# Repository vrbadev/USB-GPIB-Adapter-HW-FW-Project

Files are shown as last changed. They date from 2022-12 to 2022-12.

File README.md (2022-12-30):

# USB-GPIB Adapter (HW & FW)
 A complete hardware and firmware design of a custom USB-GPIB adapter. This project was created as a part of a semestral work of a [Virtual Instrumentation course (B3M38VIN)](https://intranet.fel.cvut.cz/en/education/bk/predmety/46/82/p4682806.html) at the Czech Technical University.

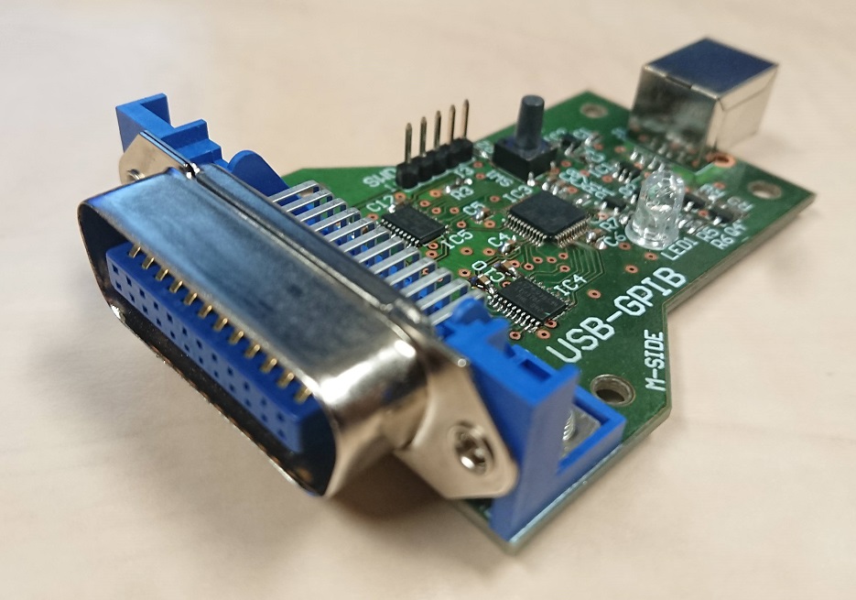
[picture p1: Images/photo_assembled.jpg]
The assembled USB-GPIB Adapter board. The assembled USB-GPIB Adapter board


## Repository Contents

* **Hardware folder** - Contains complete Altium Designer 6 PCB project, including PDF schematic and layout visualisations.
* **Firmware folder** - Contains complete Keil uVision project with the firmware for the STM32F103C6T6 microcontroller.
* **Gerber ZIP file** - An archive containing generated production files for the PCB.

## Motivation

The General Purpose Interface Bus (GPIB) is one of the most widely used communication interfaces for laboratory measuring and testing instruments. It was developed in 1965 by Hewlett-Packard (which is why it is sometimes referred to as HP-IB) and was later adopted as the IEEE 488 standard in 1975, gradually evolving into the current IEEE 488.2 standard in 1992. It also defined the SCPI (Standard Commands for Programmable Instruments) command structures, which now form a single and universal set of commands for controlling all instruments connected to this bus.

To connect the bus to the user's computer, however, a GPIB interface module is required, which is available for virtually all important types of computer buses, such as PCI or USB plug-in cards. However, both cables and GPIB interface modules (adapters) are very expensive, as they are used with expensive professional devices from companies such as Rhode & Schwartz, B&K Precision, Tektronix, HP, etc. They have no application in the mainstream consumer industry. To give a more realistic idea, Figs. 1 and 2 show commercial USB-GPIB adapters whose prices are in the tens of thousands of CZK. 

In the images below: [National Instruments GPIB-USB-HS adapter](https://cz.farnell.com/ni/778927-01/gpib-instrument-control-device/dp/3621284) (left) and [Keysight 82357B Interface USB-to-GPIB](https://cz.farnell.com/keysight-technologies/82357b/converter-interface-usb-to-gpib/dp/1425679) (right).

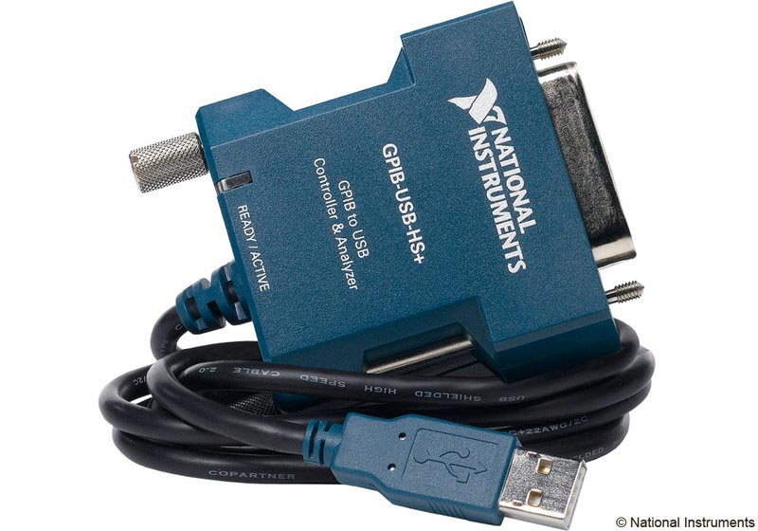
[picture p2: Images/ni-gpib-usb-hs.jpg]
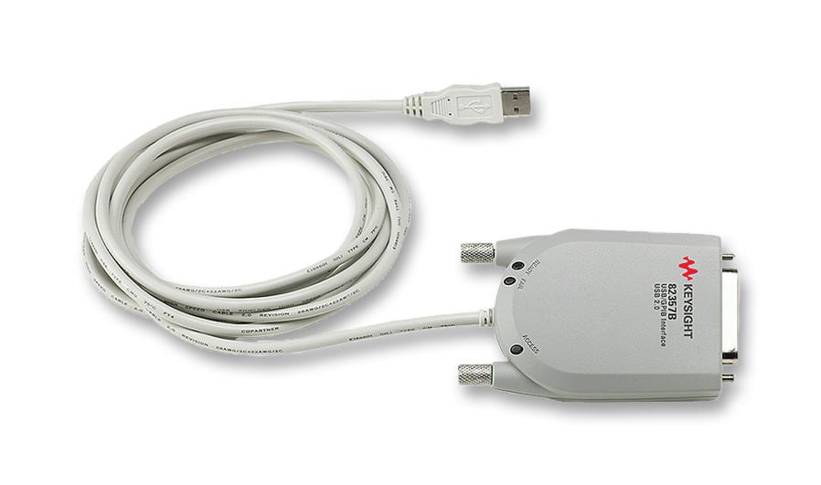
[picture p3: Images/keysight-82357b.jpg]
 

<p style="clear:both;">

For this reason, many open-source alternatives to commercial USB-GPIB adapters have already been developed that can be easily assembled and used without major problems with all laboratory instruments  with GPIB interfaces. This paper deals with the design of a similar adapter from commercially available components and is inspired by [this GitHub project](https://github.com/xyphro/UsbGpib).
</p>

## Basic Description of GPIB

GPIB is a parallel bus, i.e. each subsequent measuring instrument can be connected via a double-sided GPIB connector to the connector plugged into the previous instrument. In this way, up to 14 instruments can be connected together without a control counter (adapter). It supports a transfer rate of max. 1 MB/s. [[Tutorial Description of the Hewlett-Packard Interface Bus](http://www.bitsavers.org/pdf/hp/hpib/TutorialDescrOfHPIB.pdf)]

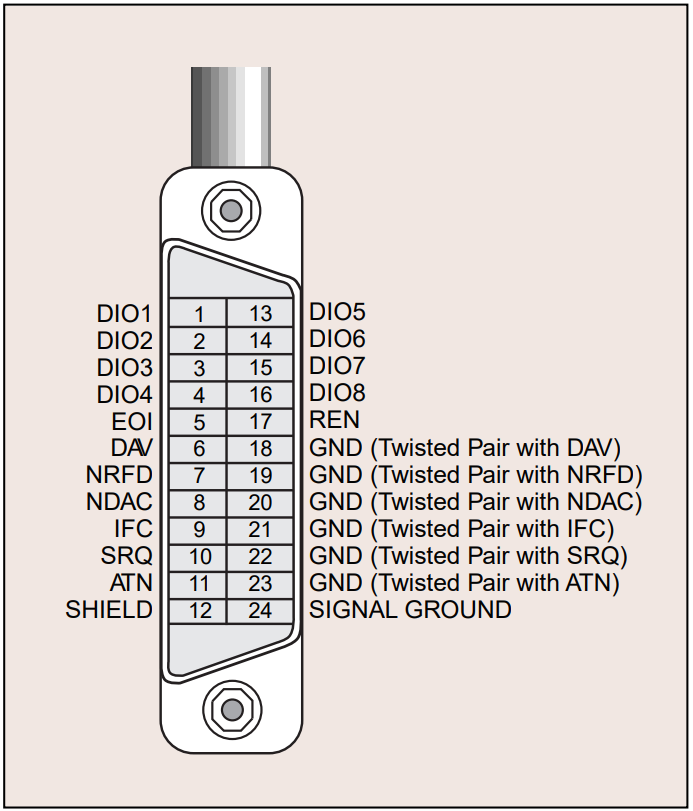
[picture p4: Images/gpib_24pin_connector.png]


The standard GPIB connector is also labeled Centronics and uses 24 wires, as indicated in the image on right (taken from the [GPIB Tutorial](http://lmu.web.psi.ch/docu/manuals/software_manuals/GPIB/GPIB_tutorial.pdf)). Eight of the 24 wires are used for grounding and the remaining wires can be divided into 3 groups:
* **8 data wires** labeled DIO1 to DIO8. They are used for data and command transmission (depending on the state of the ATN wire). All commands and most data use the 7-bit ASCII/ISO set, therefore DIO8 can be used for parity.
* **3 handshaking wires** are used for asynchronous control of the byte transfer of individual messages between devices and guarantee error-free transmission. They are NRFD (not ready for data) controlled by the receiver, NDAC (not data accepted) also controlled by the receivers and DAV (data valid) controlled by the data senders.
* **5 control wires** for controlling the flow of information through the bus, namely:
    - ATN (attention) - the Controller sets to log 1 if a command is sent over the data wires.
    - IFC (interface clear) - uses the Controller to control activity on the bus.
    - REN (remote enable) - controlled by the Controller to provide remote control.
    - SRQ (service request) - can be used by any device for asynchronous controller service request.
    - EOI (end or indentify) - used by the Talker to indicate the end of a sent message, also used by the Controller.

The bus uses inverse TTL logic, i.e. if the state of the lines is log 1 (High), the corresponding voltage is less or equal 0.8	V. The inverse of the state log. 0 (Low) corresponds to a voltage greater or equal 2.0 V. To ensure high transmission speeds, conductor lengths and distances between devices are limited, a maximum cable length of 15 m is specified, all devices should use three-state logic (log 0, log 1 and Hi-Z high impedance state) and the capacitance of each conductor should be less or equal 50 pF.

The devices connected to the GPIB bus can be divided into 3 groups:
* **Talker**, which sends data to listeners (if prompted by the Controller).
* **Listener**, which receives data (if prompted by the Controller).
* **Controller**, which manages the data flow over the bus by means of commands sent to other connected devices. Only one active Controller can be connected to the bus at a time (Controller-in-Charge, CIC).

One device (e.g. a multimeter) can be both a Talker and a Listener. The USB-GPIB adapter is the bus Controller.

### Handshaking Protocol
In the original version of the 488.1 standard, it was necessary for each Listener to set the NRFD to log. 0, then the Talker set DAV to log 1 to indicate to the Listener that data was available, and finally the Listener set NDAC to log. 0 after receiving a byte of data, as in the left figure below (taken from the [GPIB Tutorial](http://lmu.web.psi.ch/docu/manuals/software_manuals/GPIB/GPIB_tutorial.pdf)). This caused a time delay of T1 before the whole process could be repeated and another byte of data could be sent.

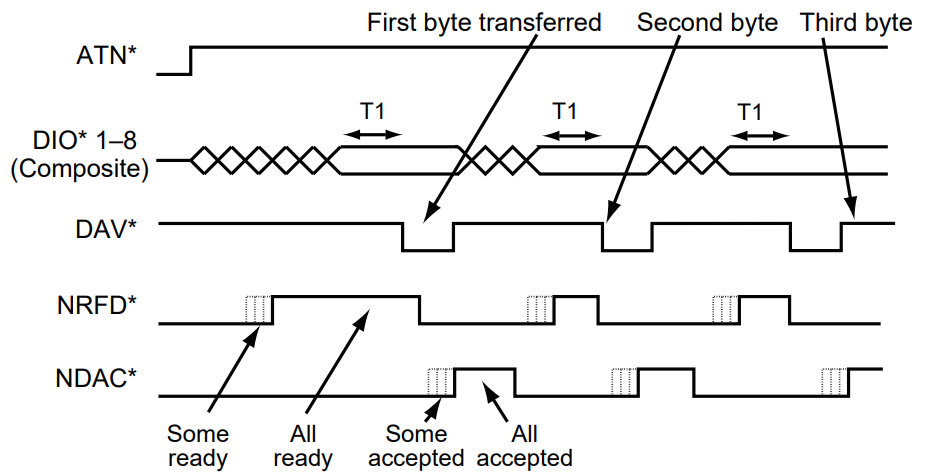
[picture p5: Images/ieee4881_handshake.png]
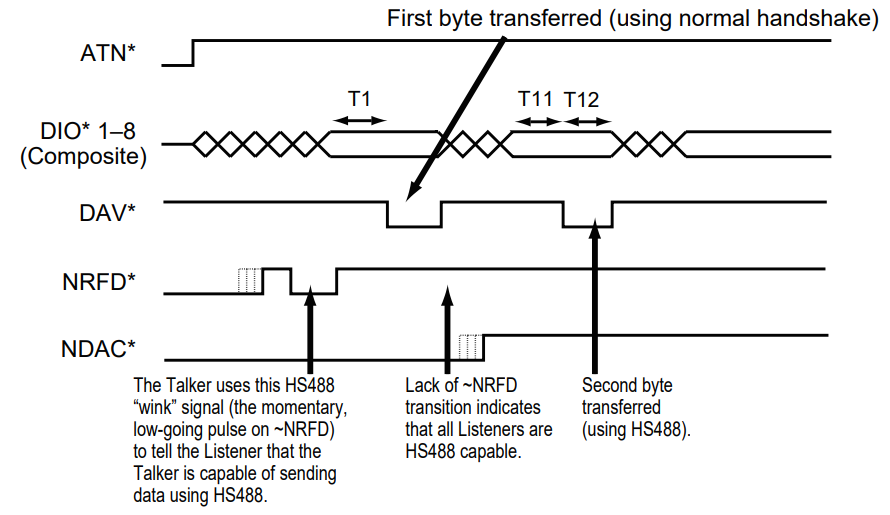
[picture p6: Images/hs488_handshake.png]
 

<p style="clear:both;">

To accelerate data transfer (up to 8 MB/s) over the GPIB bus, National Instruments developed the High-Speed GPIB Handshake Protocol called HS488. In this case, the Talker first creates a pulse (log 0) on the NRFD wire (after the controller addresses all listeners) to indicate that it can use HS488. Then the Talker moves the first byte to the data wires, waits the preset time, and sets DAV to log 1. Then it waits again, sets DAV to log. 0 and moves the next byte to the data wires, as in the right figure above (taken from the [GPIB Tutorial](http://lmu.web.psi.ch/docu/manuals/software_manuals/GPIB/GPIB_tutorial.pdf)). The Listener leaves the NDAC in log. 1 and must be able to receive single bytes at the preset delays. The Listener can pause the byte transmission by setting the NDAC to log. 0. If the Listener does not support HS488 and wants to use the normal handshake protocol, it creates a pulse log. 0 on the NRFD line.
</p>

Due to the hardware nature of this project, I will not describe further here the control commands and sequences of the cont- roler, protocols (composed of multiple control sequences), the SCPI language, or other software aspects of the GPIB bus.

## Adapter Hardware Design

[The aforementioned GitHub project](https://github.com/xyphro/UsbGpib) uses the [ATMega32U4 microcontroller from Microchip](https://www.microchip.com/content/dam/mchp/documents/OTH/ProductDocuments/DataSheets/Atmel-7766-8-bit-AVR-ATmega16U4-32U4_Datasheet.pdf). This 8-bit microprocessor offers 32 kB of FLASH memory and 2.5 kB of SRAM memory and is based on the AVR architecture. It contains a USB peripheral, an internal 8 MHz oscillator and a maximum core operating frequency of 16 MHz (16 MIPS). The advantage is the power supply voltage of a 5 V and the corresponding voltage tolerance of the GPIO pins in the input and output configuration.

For my design I chose the [STM32F103C6T6 microprocessor from STMicroelectronics](https://www.st.com/resource/en/datasheet/stm32f103c6.pdf). It is a 32-bit microprocessor also with 32 kB of FLASH memory and 10 kB of SRAM memory, built on ARM architecture with Cortex-M3 core. It also offers a USB peripheral and an internal 8 MHz RC oscillator that can be used with an integrated PLL to obtain a maximum operating frequency of 72 MHz. However, it must be powered from 3.3 V and most GPIOs are 5 V tolerant (denoted FT) in the input configuration only. I selected it for the easy soldering of its LQFP48 package.

### USB Connector

For connecting USB peripherals, I chose a USB 2.0 B female connector, which is standard for USB endpoint devices. To provide ESD protection, a [USBLC6-2 component from STMicroelectronics](http://www.st.com/resource/en/datasheet/usblc6-2.pdf) is added. The wiring diagram is shown below.

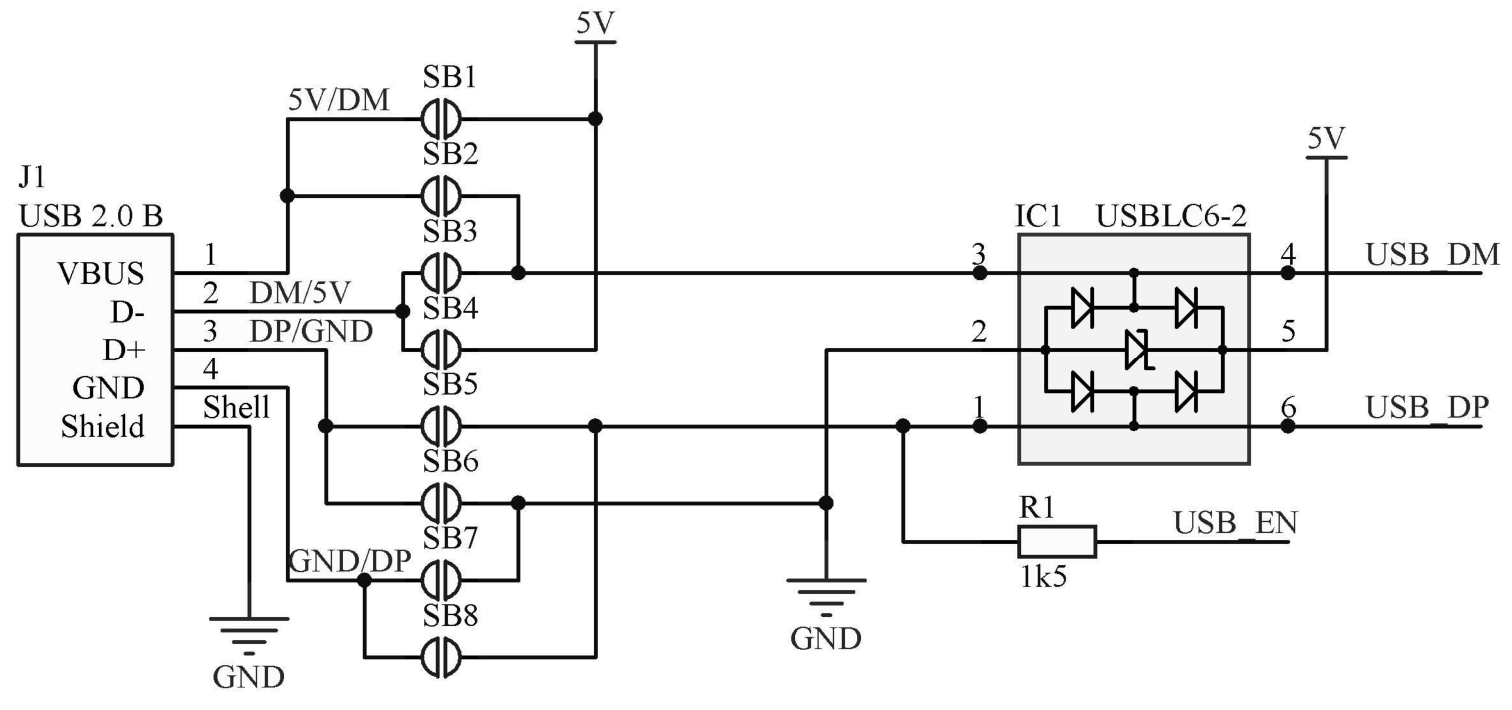
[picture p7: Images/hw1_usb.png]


The USB_DM and USB_DP lines are connected directly to the microprocessor. The USB_EN line with a 1.5kOhm pull-up resistor on the USB D+ line is used to trigger enumeration as a Full-Speed USB Device (according to the USB FS specification), since STM32 microprocessors do not internally contain this resistor.

To be able to use GPIB socket or plug and thus to fit components from both sides (the socket pins are axially inverted to the plug pins), I made the PCB design axially symmetrical in respect to the placement of THT components. Because if the USB connector is soldered from the other side, the +5V contact is then swapped with GND, similarly D- with D+, so shorting jumpers SB1 to SB8 are added to resolve this problem. These jumpers (i.e. odd or even) should be closed on the side of the PCB where the USB connector will be mounted.

### Power Circuit

To obtain 3.3 V from 5 V (USB) I chose a linear regulator with output current up to 300 mA, low dropout, minimum quiescent current and fixed output voltage, [LDK130 from STMicroelectronics](https://www.st.com/resource/en/datasheet/ldk130.pdf). Blocking capacitors of 100 nF are added at all power supply pins of the ICs in the circuit. The schematic is shown in figure below.

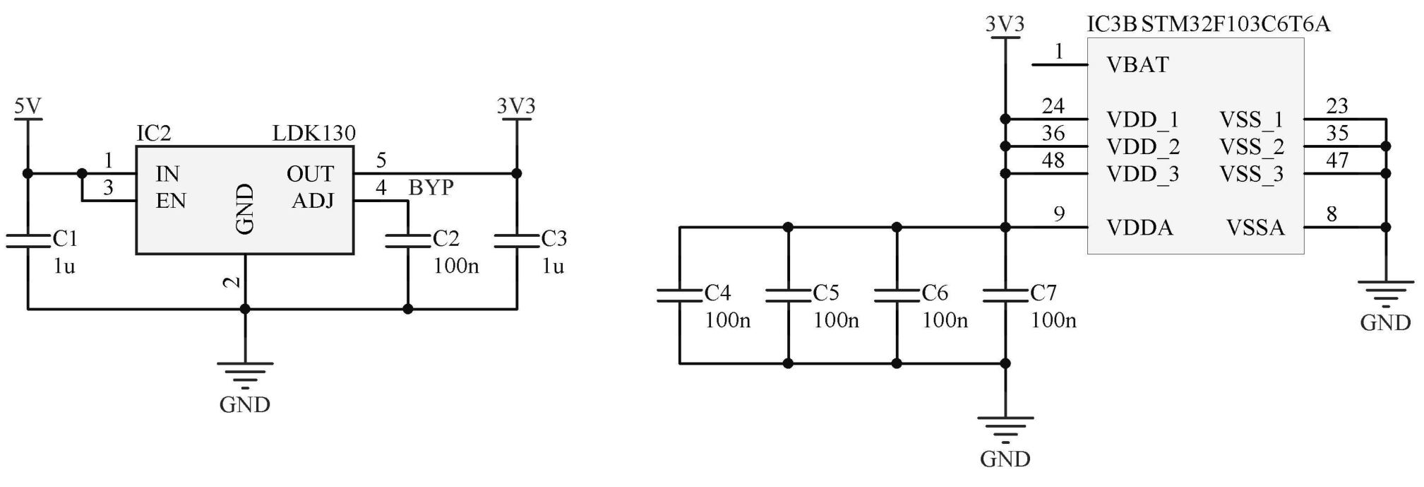
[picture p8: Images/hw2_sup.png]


### STM32 Microcontroller

Since the internal RC oscillator is be used, pins PD0 and PD1 remain unconnected. Pull-up resistor R2 keeps log. 1 on the reset pin of the microcontroller and button SW1 is used to ground and reset it, capacitor C8 is placed here to filter out mechanical oscillations of the button. Pull-down resistor R3 on the BOOT0 pin is used to initially load the program from the microprocessor's FLASH memory.

STM32 processors are programmed via the SWD interface and the ST-Link programmer, which consists of the SWDCLK and SWDIO pins in addition to the reset pin, power and ground. These 5 wires are routed through the J3 connector in the same order as they are found, for example, on Nucleo boards. The wiring of this part is shown below.

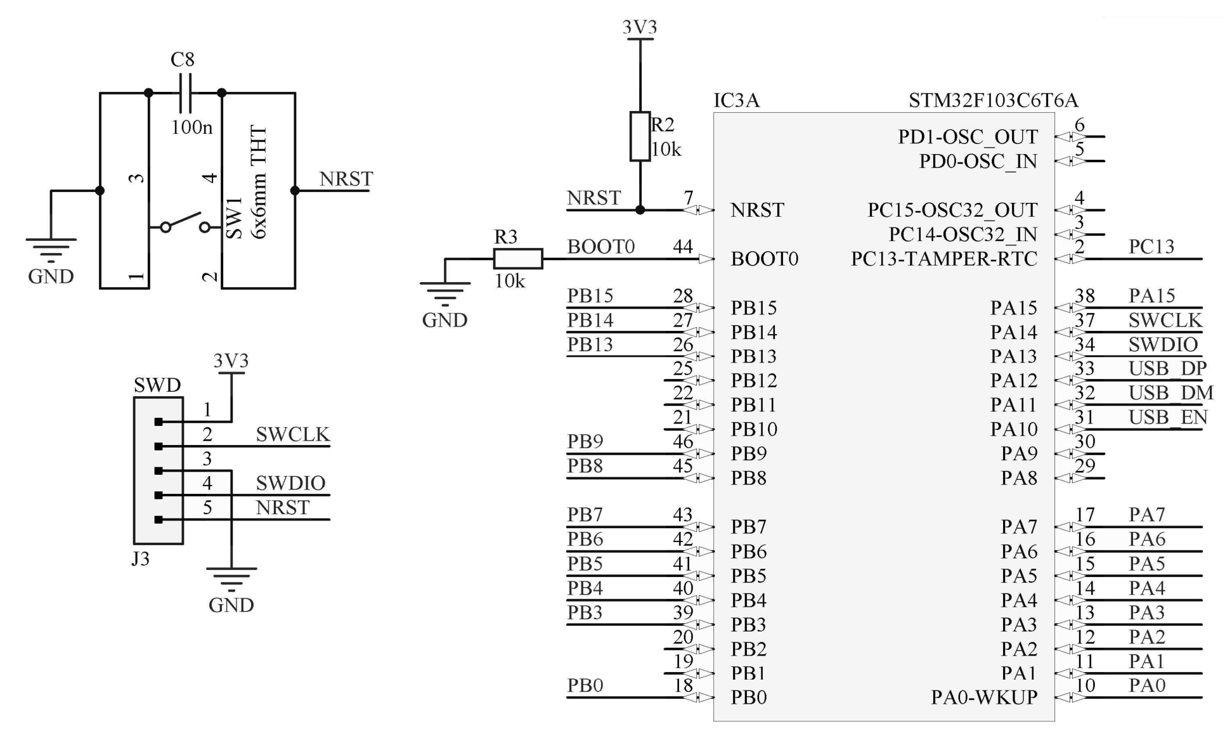
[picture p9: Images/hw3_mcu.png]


### RGB Indication LED

For the indication of the adapter's status I chose an RGB LED with a common anode with a package size of 5 mm.

Individual internal LEDs are switched via MOSFET N-channel transistors of type BSS138. An inverter consisting of transistor Q1 and resistor R7 ensures that the red component of the RGB LED is lit immediately after power is connected, and can be turned off using log. 1 on pin PB13. The schematic is shown below.

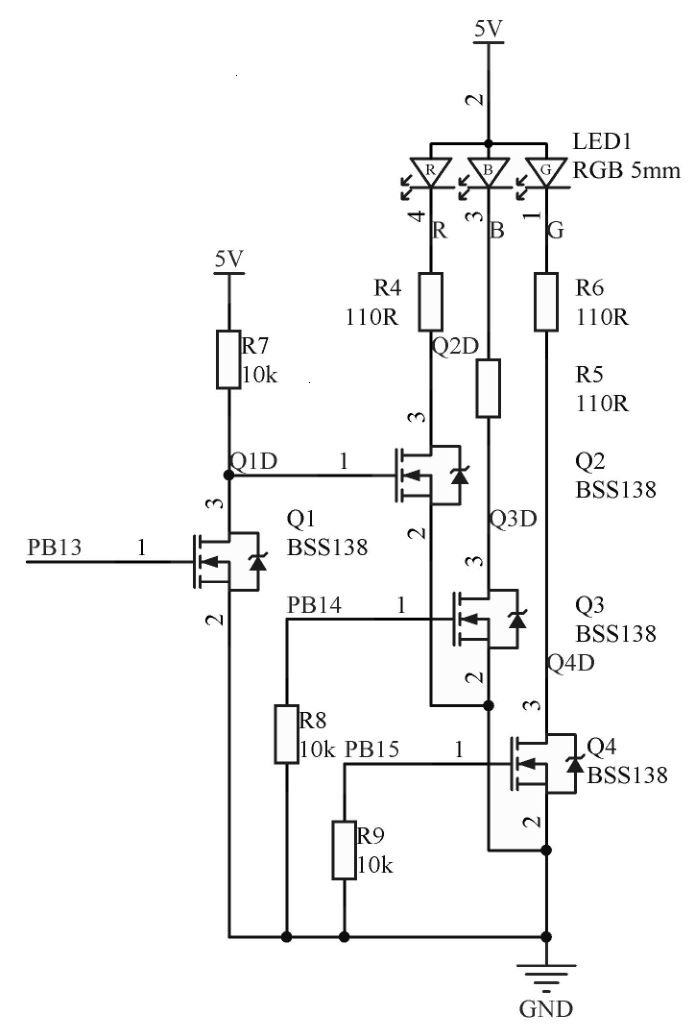
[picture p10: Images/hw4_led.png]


### GPIB Connector

The microprocessor GPIOs PA0 to PA7 are assigned to the data wires D1 to D8 of the GPIB bus. The remaining bus wires are assigned to GPIOs PB3 to PB9 and PA15. To add 5V tolerance to the microprocessor outputs and ESD protection to the bus wires, two [ST2378E 8-bit level-translators](https://www.st.com/resource/en/datasheet/cd00003335.pdf) (3.3V to 5V logic level converters) from STMicroelectronics are used. They are designed for bidirectional asynchronous data transfers up to 13 Mbps. The GPIOs of the microcontroller PB0 and PC13 are connected to the OE (Output Enable) pins, which are used to enable/disable these converters.

The bus wires are shuffled on the pins of these ICs to interface the pins of the microprocessor package while minimising the number of necessary vias. To ensure similar path impedance, the first IC is designated for the data lines and the second IC for the control lines. The schematic is shown below.

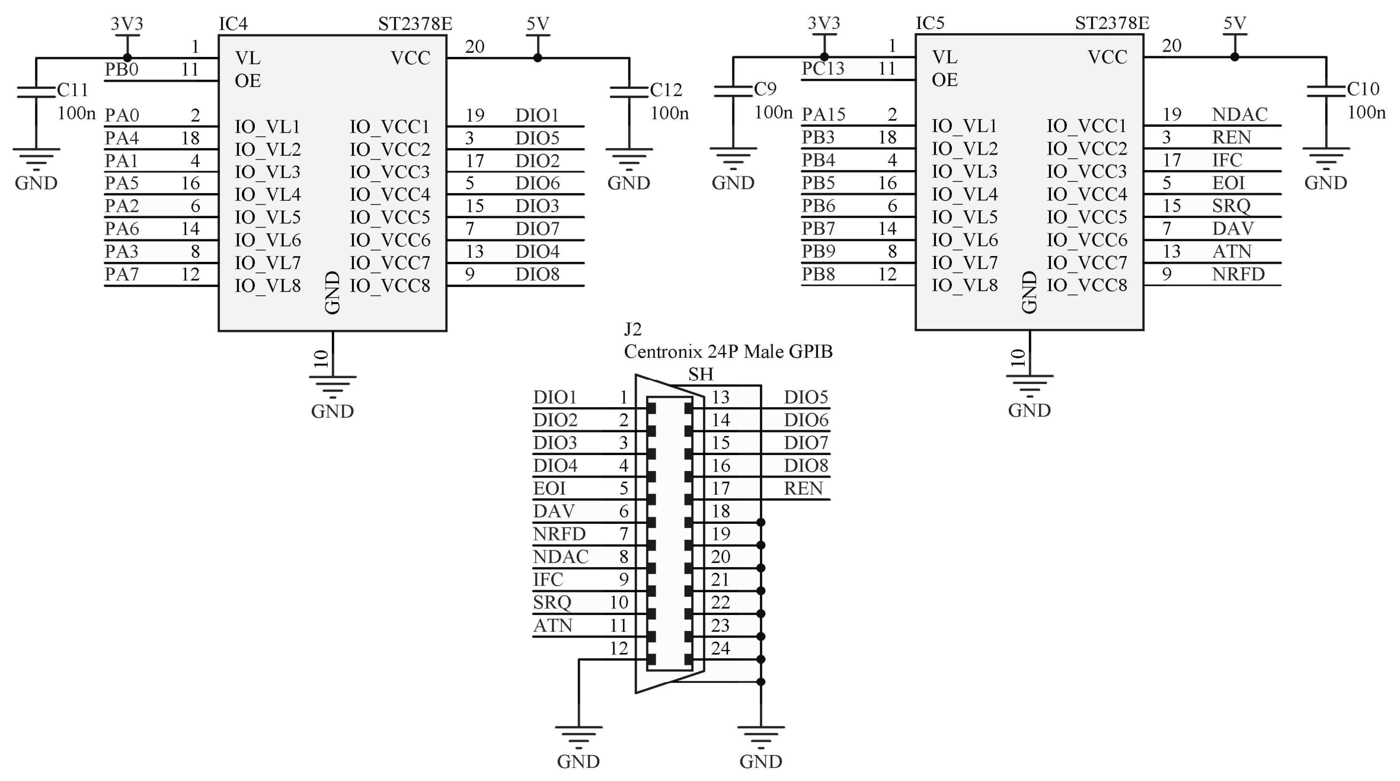
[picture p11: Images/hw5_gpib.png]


### Layout Visualisation

Top and bottom views of the layout are shown below. The PCB size is approximately 71.1x55.9 mm. If an adapter case is designed (e.g. for 3D printing), 3.2mm mounting holes in the corners can be used for its attachment. THT components mounted on the top side or on the bottom side of the PCB should always fit into a printed case the same way for both cases.

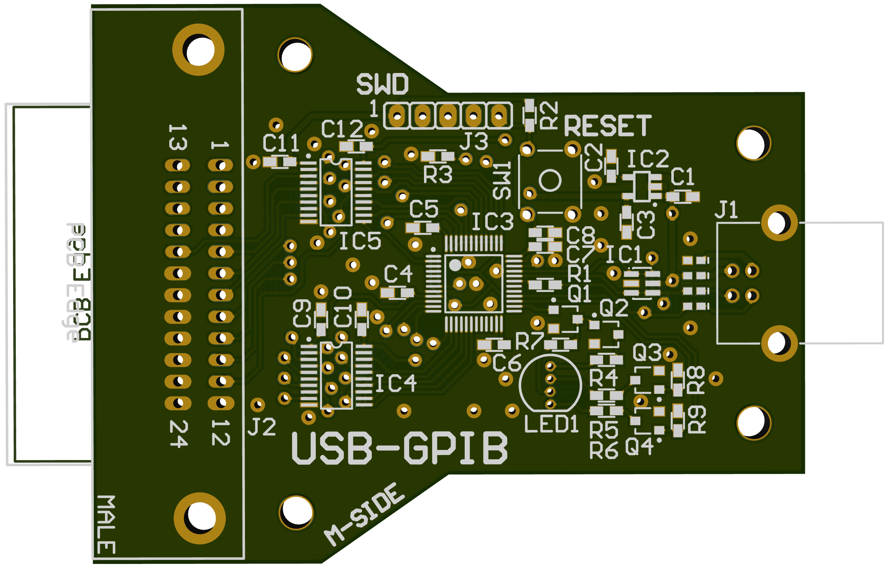
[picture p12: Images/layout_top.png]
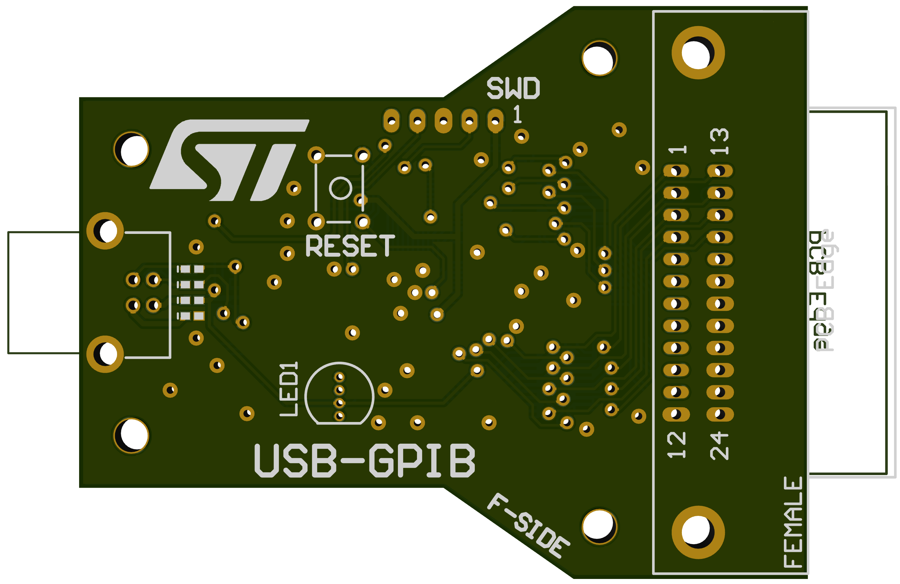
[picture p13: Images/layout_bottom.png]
 

### Bill of Material (BOM)

| **IDs**     | **Pcs** | **Value/Type**                                | **Description**              | **Package** |
|-------------|---------|-----------------------------------------------|------------------------------|-------------|
| C1,C3       | 2       | 1u                                            | Ceramic capacitor            | 0603        |
| C2,C4-C12   | 10      | 100n                                          | Ceramic capacitor            | 0603        |
| IC1         | 1       | USBLC6-2SC6                                   | ESD protection for USB       | SOT23-6     |
| IC2         | 1       | LDK130M33R                                    | LDO regulator 3.3V/300mA     | SOT23-5     |
| IC3         | 1       | STM32F103C6T6                                 | 32-bit MCU                   | LQFP-48     |
| IC4,IC5     | 2       | ST2378ETTR                                    | Voltage-level translator     | TSSOP-20    |
| J1          | 1       | WE 61400416121                                | USB 2.0 B female connector   | 4-pin       |
| J2 (male)   | 1       | NorComp 112-024-113R001                       | GPIB Centronics plug         | 24-pin      |
| J2 (female) | 1       | NorComp 112-024-213R001<br>CONNFLY DS1079-F240BS | GPIB Centornics socket       | 24-pin      |
| J3          | 1       | RM2.54mm                                      | Pin header                   | 5-pin       |
| LED1        | 1       | RGB                                           | Common anode LED             | 5mm         |
| SW1         | 1       | KLS TS6601-13.5-180                           | Microswith (ON)-OFF          | 6x6mm       |
| R1          | 1       | 1k5                                           | Resistor                     | 0603        |
| R2,R3,R7-R9 | 5       | 10k                                           | Resistor                     | 0603        |
| R4-R6       | 3       | 110R                                          | Resistor                     | 0603        |
| Q1-Q4       | 4       | BSS138                                        | N-Channel logic-level MOSFET | SOT23-3     |

## Firmware Description

### USB Test and Measurement Class (USBTMC)

The documentation of the USBTMC class and the USB endpoints and packets used is available [in an archive at usb.org](http://www.usb.org/sites/default/files/USBTMC_1_006a.zip), including the documentation of the USBTMC subclass USB488. The details of data transfer from USB to GPIB bus, supported commands and behaviour according to the official [IEEE 488.1](https://doi.org/10.1109/ieeestd.1988.81527) and [IEEE 488.2](https://doi.org/10.1109/ieeestd.1992.114468) standards are described in the following text.

Endpoints are basically sections of the memory of the connected USB device (e.g. USB-GPIB adapter), which are accessed by the host (e.g. user PC) and written to/read from, i.e. they are USB protocol communication channels. According to the documentation, every USB device of the TMC class implements these endpoints:
* Control endpoint (mandatory) - used to control the device by the host, data is written and read according to the USB 2.0 protocol documentation, its serial number is always 0x00.
* Bulk-OUT (mandatory) - for writing data to the device (i.e. Host-To-Device).
* Bulk-IN (mandatory) - for reading data from the device (i.e. Device-To-Host).
* Interrupt-IN (optional) - uses the device to notify the host of events (for subclass USB488), e.g. when an SRQ is detected on the GPIB bus.

The messages defined by the TMC class that are written and read by the host from endpoints on the device have a fixed structure that typically consists of the message type (MsgID, 0 to 255), an incremented transfer identifier (bTag and bTagInverse, 0 to 255), and the content according to the message type.

An example of a message type (without a defined device response) is `DEV_DEP_MSG_OUT`, which is written by the host to the Bulk-OUT endpoint and contains the number of bytes to be transmitted and the message (or part of the message). In contrast, the `REQUEST_DEV_DEP_MSG_IN` message type is used by the host when it wants to request the device to send a response, i.e. to write a `DEV_DEP_MSG_IN` message to the Bulk-IN endpoint. These are all 3 types of device dependent messages, similarly 3 types of vendor dependent messages are defined. For Bulk endpoints, these are all message types defined by the TMC class and are used to transfer commands/measured data (in the same format as on the GPIB bus).

In addition, the USB488 subclass specifies the TRIGGER message type (to Bulk-OUT, no defined response) and is used for synchronization. I.e. on receipt, the adapter generates a GET command on the GPIB bus. This message corresponds to sending the "*TRG" command with a message of type `DEV_DEP_MSG_OUT`.

The TMC documentation also describes the methods of splitting, interrupting and blocking transmissions, then requirements for repeating certain messages, packet formats with settings and how the capabilities of the connected device (Setup, Capabilities) are written to the Control endpoint, the use of the Interrupt-IN endpoint etc.

### Examples of TMC communication

An example taken from the [USB Device Test and Measurement Class Specification](http://www.usb.org/sites/default/files/USBTMC_1_006a.zip) is passing the identification command `"*IDN?"` to a connected USB device (e.g. USB-to-GPIB adapter). In this case, the host writes a message of type DEV_DEP_MSG_OUT with the contents shown in the below figure to the Bulk-OUT endpoint.

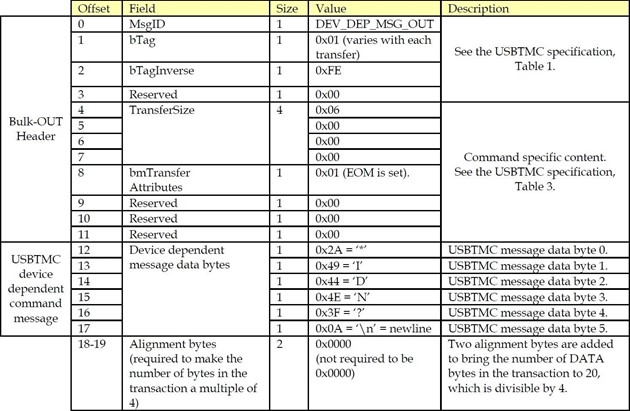
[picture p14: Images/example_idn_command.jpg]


Then the host writes into the Bulk-OUT register another message (another transfer, that is why the bTag is 0x02) of the `REQUEST_DEV_DEP_MSG_IN` type - requesting a response from the device (adapter), with the content shown in the figure below.

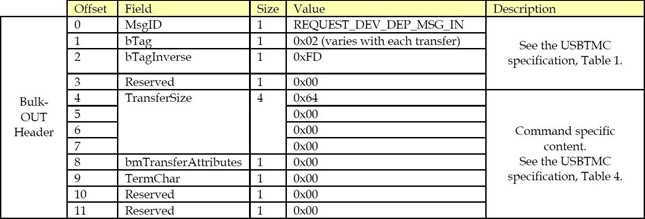
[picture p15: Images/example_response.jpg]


Eventually, the device (adapter) responds by writing into the Bulk-IN register a message of the `DEV_DEP_MSG_IN` type containing the identification of the measuring device (the bTag value is still 0x02) e.g. `"XYZCO,246B,S-0123-02,0\n"` (according to the format in the [IEEE Std 488.2-1992](https://doi.org/10.1109/ieeestd.1992.114468), ch. 10.14), with the content shown in the figure below.

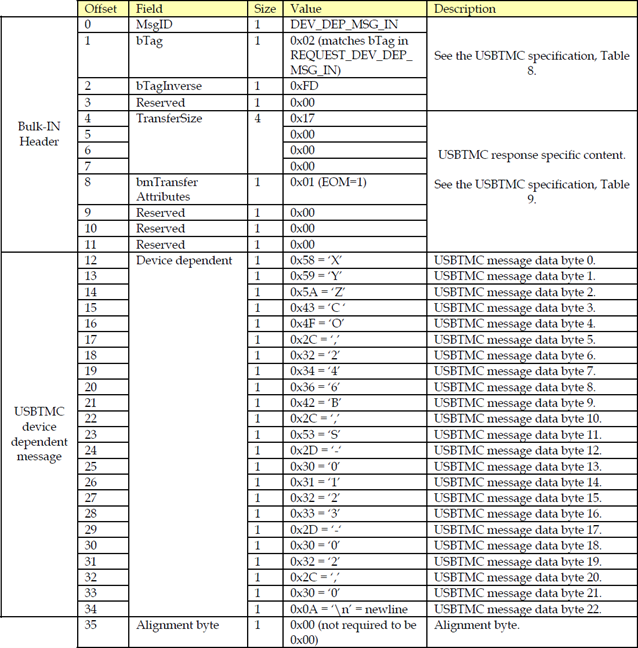
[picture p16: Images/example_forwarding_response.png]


Thanks to the fact that the content of the TMC messages corresponds to the content of the communication over the GPIB bus, the adapter is very simple in terms of firmware. The USB-GPIB adapter only interprets the incoming TMC messages by controlling the bus wires appropriately using GPIO, similarly reading the data from the bus and passing it to the host (user PC). The TMC class standard is also fully compatible with common software designed for GPIB control, such as NI-VISA or LabView.

To use the USBTMC class in this project it was advisable to use the existing open-source library [TinyUSB](https://github.com/hathach/tinyusb) or [LIBUSB](https://github.com/dmitrystu/libusb_stm32), as both already contain implementations of this class, including the necessary definitions and USB descriptors, and also support STM32 microprocessors.

### GPIO Control of the GPIB Bus

The procedures for controlling the GPIB bus wires using GPIO were taken from the aforementioned GitHub project. LOW states mean log. 1 (True), HIGH states mean log. 0 (False), i.e. according to the voltage on the bus wires. I only list here the 2 most important procedures implementing the handshaking protocol, namely for sending a byte over the bus and reading a byte from the bus.

Then it is possible to use the commands to e.g. test the listener addresses (setting the active listener by the LAG command on each address in turn and test the reaction to the ATN change to HIGH by waiting for the NDAC change to LOW) and thus find all the measurement devices connected to the GPIB bus (if there is no listener on the given address, the NDAC remains HIGH).

#### Pseudocode: Sending a byte over the bus

```
DAV, NRFD, NDAC ← HIGH (default)
if COMMAND then
    ATN ← LOW
else
    ATN ← HIGH
end if
DIO1.. 8 ← BYTE
Wait until NRFD ← HIGH (ready for data)
DAV ← LOW (data available)
Wait until NDAC ← HIGH (data accepted)
DAV ← HIGH (data not available)
Release DIO1... 8
ATN ← HIGH (default)
```

#### Pseudocode: Reading a byte from the bus

```
NDAC ← LOW (data not accepted)
NRFD ← HIGH (ready for data)
Wait until DAV ← LOW (data available)
NRFD ← LOW (not ready for data)
BYTE ← DIO1.. 8
NDAC ← HIGH (data accepted)
Wait until DAV ← HIGH (data not available)
if EOI is LOW then
    Transfer terminated (last byte)
end if
```

## Todo List

* Finish the USB TMC class implementation in the FW project (as a USB composite device). Currently, only the USB CDC implementation works.

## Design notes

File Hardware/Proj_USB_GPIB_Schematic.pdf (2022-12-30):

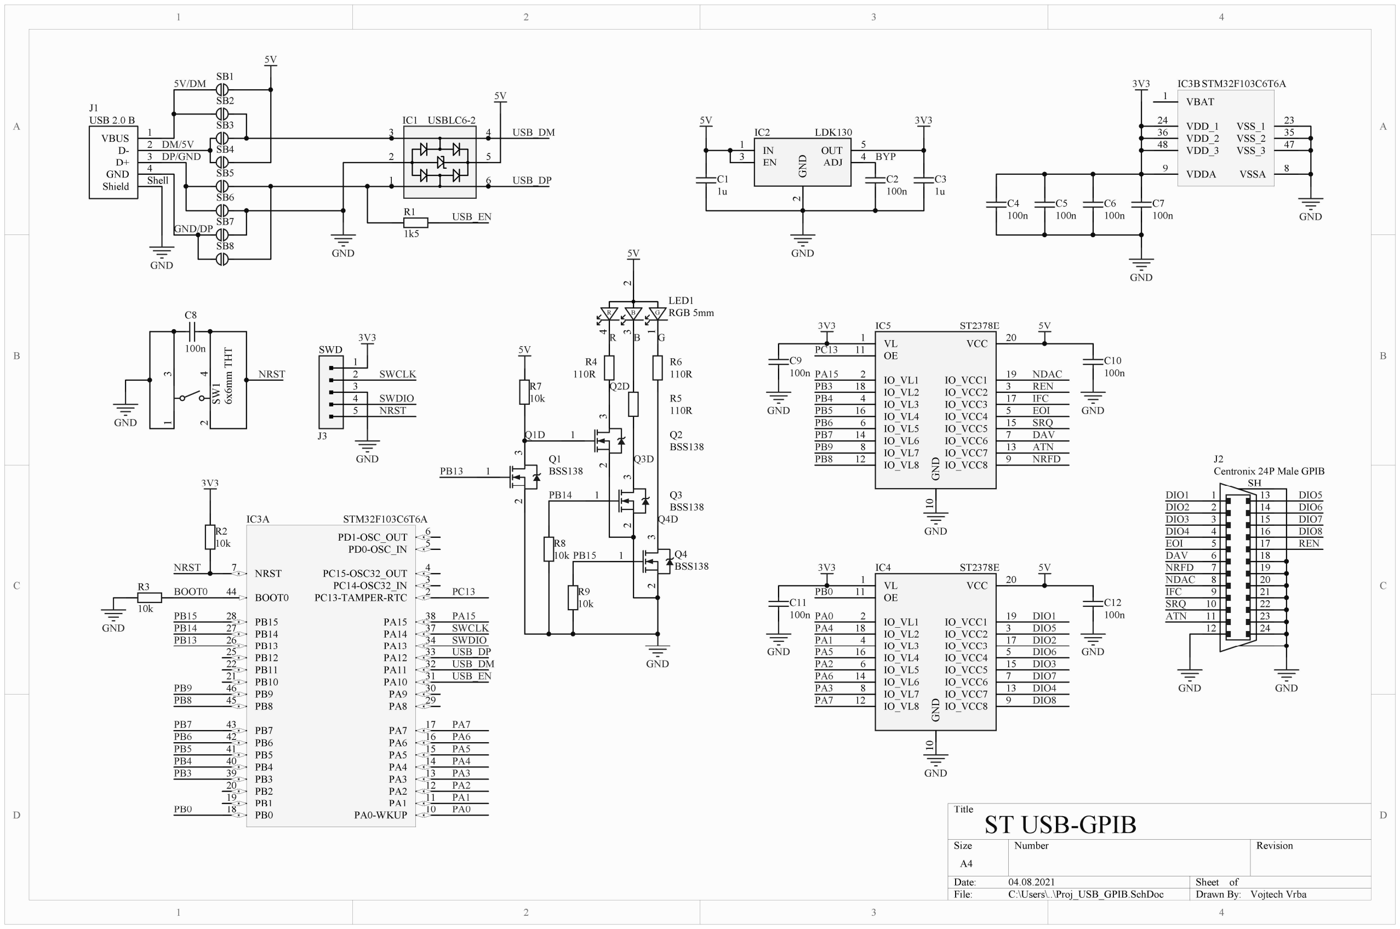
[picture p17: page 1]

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
Title

Size | Number | Revision
A4
Date: | 04.08.2021 | Sheet of
File: | C:\Users\..\Proj_USB_GPIB.SchDoc | Drawn By:

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
12 24

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
Centronix 24P Male GPIB
PC13-TAMPER-RTC | 2
PC14-OSC32_IN | 3
PC15-OSC32_OUT | 4
PD0-OSC_IN | 5
PD1-OSC_OUT | 6

NRST 7

PA0-WKUP | 10 PA1 | 11 PA2 | 12 PA3 | 13 PA4 | 14 PA5 | 15 PA6 | 16 PA7 | 17
PB0 18 | PB1 19 | PB2 20
PB10 21 | PB11 22 | PB12 25 | PB13 26 | PB14 27 | PB15 28
PA8 | 29 PA9 | 30 PA10 | 31 PA11 | 32 PA12 | 33 PA13 | 34 PA14 | 37 PA15 | 38
PB3 39 | PB4 40 | PB5 41 | PB6 42 | PB7 43

BOOT0 44

PB8 45 | PB9 46
IC3A | STM32F103C6T6A

VBAT 1

VSSA | 8 VDDA 9
VSS_1 | 23 VDD_1 24
VSS_2 | 35 VDD_2 36
VSS_3 | 47 VDD_3 48

IC3BSTM32F103C6T6A

1

2

3 4

5

6

IC1 USBLC6-2

IN 1
EN 3 | GND

2

ADJ | 4
OUT | 5
IC2 | LDK130

IO_VL1 2
IO_VL2 18
IO_VL3 4
IO_VL4 16
IO_VL5 6
IO_VL6 14
IO_VL7 8
IO_VL8 12
IO_VCC1 | 19
IO_VCC2 | 3
IO_VCC3 | 17
IO_VCC4 | 5
IO_VCC5 | 15
IO_VCC6 | 7
IO_VCC7 | 13
IO_VCC8 | 9
VL 1 | VCC | 20
OE 11 | GND 10
IC4 | ST2378E

IO_VL1 2
IO_VL2 18
IO_VL3 4
IO_VL4 16
IO_VL5 6
IO_VL6 14
IO_VL7 8
IO_VL8 12
IO_VCC1 | 19
IO_VCC2 | 3
IO_VCC3 | 17
IO_VCC4 | 5
IO_VCC5 | 15
IO_VCC6 | 7
IO_VCC7 | 13
IO_VCC8 | 9
VL 1 | VCC | 20
OE 11 | GND 10
IC5 | ST2378E
VBUS | 1
D- | 2
D+ | 3
GND | 4
Shield | Shell

J1
USB 2.0 B

5V

5V

GND

5V

GND

1u

C1
100n

C2
1u

C3

3V3

DIO1 | DIO5 DIO6 DIO7 DIO8 REN
DIO2
DIO3
DIO4
EOI
DAV
NRFD
NDAC
IFC
SRQ
ATN
GND | GND

USB_DM

USB_DP

1k5

R1 | USB_EN | 100n C4
100n

C5
100n

C6

USB_DM

USB_DP

SWDIO

SWCLK

USB_EN

GND

GND

100n

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
NRST

GND

100n

C8

NRST

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
DIO1

DIO2

DIO3

DIO4

DIO5

DIO6

DIO7

DIO8

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
NRFD

NDAC

IFC

SRQ

ATN

PA15

PB9
PB8

PB7
PB6
PB5
PB4
PB3

PA15
PB3
PB4
PB5
PB6
PB7

PB8

PB9 ³ ¹ | 2 4 SW¹ 6x6mm THT

PC13

100n

C9
100n

C10

100n

C11
100n

C12

GND | GND
GND | GND

3V3

3V3

5V

5V

PC13

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
SWCLK

SWDIO
NRST

BYP

BOOT0

2

4

3

1

R | B | G

LED1
RGB 5mm 2

1 3
Q1
BSS138 2

1 3
Q2
BSS138 2

1 3
Q3
BSS138 2

1 3
Q4
BSS138

5V

110R

R4

110R

R5

110R

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
PB14

PB15

PB13

PB15
PB14
PB13
R | B | G

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
5V/DM

DM/5V
DP/GND

GND/DP

# ST USB-GPIB

Vojtech Vrba

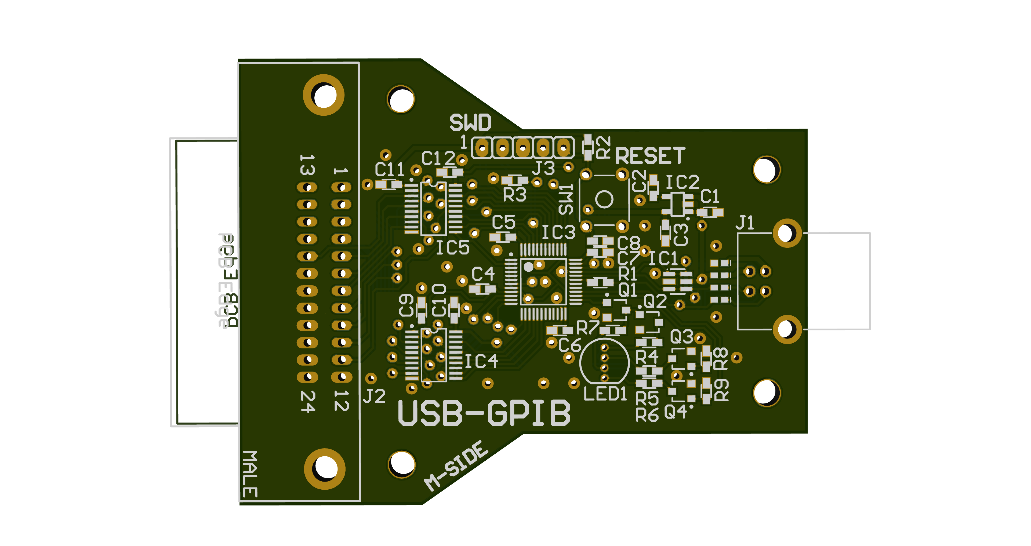
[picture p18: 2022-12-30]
Hardware/Proj_USB_GPIB_layout_top.png

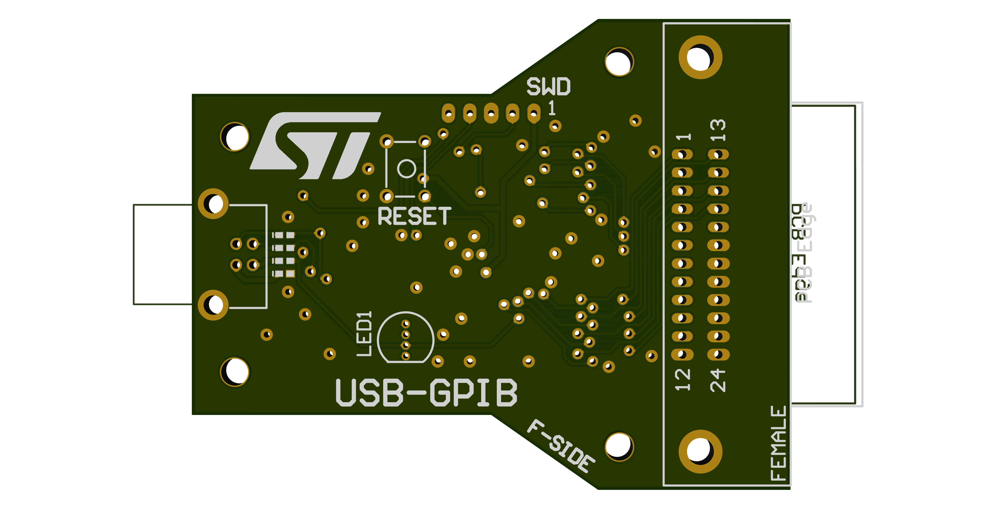
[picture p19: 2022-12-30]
Hardware/Proj_USB_GPIB_layout_bottom.png

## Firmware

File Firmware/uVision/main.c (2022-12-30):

#include "stm32f103x6.h"
#include "delay.h"
#include "usblib.h"
#include "gpio.h"

#define USB_DM PA11
#define USB_DP PA12
#define USB_EN PA10

#define LED_R PB13
#define LED_B PB14
#define LED_G PB15

volatile bool EVENT_1HZ = false;
volatile bool EVENT_10HZ = false;
volatile bool EVENT_100HZ = false;
volatile bool EVENT_1000HZ = false;
volatile bool EVENT_TIMEOUT = false;

/* USB setup */
void usb_setup(void)
{	
	// PA11 as DM, PA12 as DP
	gpio_mode(USB_DM, GPIO_MODE_OUTPUT_50MHZ, GPIO_CNF_OUTPUT_ALTERNATE_OPEN_DRAIN);
	gpio_mode(USB_DP, GPIO_MODE_OUTPUT_50MHZ, GPIO_CNF_OUTPUT_ALTERNATE_OPEN_DRAIN);
	
	// PA10 as controllable 1k5 pull-up at DP line for enumeration control
	gpio_mode(USB_EN, GPIO_MODE_OUTPUT_2MHZ, GPIO_CNF_OUTPUT_GENERAL_PUSH_PULL);
	gpio_write(USB_EN, 0);
  USBLIB_Init();
	gpio_write(USB_EN, 1);
}


/*
HSI frequency RC osc: 8MHz
PLL (x12) -> MCU frequency is (8MHz / 2) * 12 = 48 MHz
*/
void rcc_init(void)
{
	RCC->CR |= RCC_CR_HSION;
	while ((RCC->CR & RCC_CR_HSIRDY) == 0);
	
	// Change System Clock to HSI
	RCC->CFGR &= ~RCC_CFGR_SW;
  while ((RCC->CFGR & RCC_CFGR_SWS) != 0);
		
	// Turn on external clock (HSE)
	//RCC->CR |= RCC_CR_HSEON;
	//while ((RCC->CR & RCC_CR_HSERDY) == 0);
	
	// Set flash memory access latency to 2 cycles + enable prefetch buffer
	FLASH->ACR = FLASH_ACR_LATENCY_2 | FLASH_ACR_PRFTBE;
	
	// PLL input clock (4MHz) x 12
	RCC->CFGR |= RCC_CFGR_PLLMUL12;
	
	// HSE as PLL input clock
	//RCC->CFGR |= RCC_CFGR_PLLSRC; 
	
	// Clock for APB1 divided 2x (to get 24MHz)
	RCC->CFGR |= RCC_CFGR_PPRE1_2;
	
	// USB clock not divided by 1.5x
	RCC->CFGR |= RCC_CFGR_USBPRE;
	
	// Turn on PLL
	RCC->CR |= RCC_CR_PLLON;
	while ((RCC->CR & RCC_CR_PLLRDY) == 0);
	
	// Change main clock to PLL
	RCC->CFGR = (RCC->CFGR & ~RCC_CFGR_SW) | RCC_CFGR_SW_PLL;
	while ((RCC->CFGR & RCC_CFGR_SWS) != RCC_CFGR_SWS_PLL);
	
	// Disable internal clock to save power
	//RCC->CR &= ~RCC_CR_HSION;
	
	// Disable LSE clock
	RCC->BDCR &= ~RCC_BDCR_LSEON;
}

int main(void)
{
	rcc_init();
	gpio_init();
	stk_init();
	usb_setup();
	
	gpio_mode(LED_R, GPIO_MODE_OUTPUT_50MHZ, GPIO_CNF_OUTPUT_GENERAL_PUSH_PULL);
	gpio_mode(LED_B, GPIO_MODE_OUTPUT_50MHZ, GPIO_CNF_OUTPUT_GENERAL_PUSH_PULL);
	gpio_mode(LED_G, GPIO_MODE_OUTPUT_50MHZ, GPIO_CNF_OUTPUT_GENERAL_PUSH_PULL);
	
	gpio_write(LED_R, 1);
	gpio_write(LED_B, 0);
	gpio_write(LED_G, 0);
	
	int i = 0;
	while(1) {		
		if (EVENT_10HZ) {
			EVENT_10HZ = false;
		}
		
		if (EVENT_1HZ) {
			EVENT_1HZ = false;
		}
	}
}

void uUSBLIB_DataReceivedHandler(uint16_t *Data, uint16_t Length)
{
	// simple echo
	USBLIB_Transmit(Data, Length);
}

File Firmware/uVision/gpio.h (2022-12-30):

#ifndef GPIO_H_
#define GPIO_H_

#include "stm32f103x6.h"

typedef struct {
	GPIO_TypeDef* base;
	uint8_t pin;
} pin_t;


#define GPIO_CNF_INPUT_ANALOG 0
#define GPIO_CNF_INPUT_FLOATING 1
#define GPIO_CNF_INPUT_PULL_DOWN 2
#define GPIO_CNF_INPUT_PULL_UP 3

#define GPIO_CNF_OUTPUT_GENERAL_PUSH_PULL 0
#define GPIO_CNF_OUTPUT_GENERAL_OPEN_DRAIN 1
#define GPIO_CNF_OUTPUT_ALTERNATE_PUSH_PULL 2
#define GPIO_CNF_OUTPUT_ALTERNATE_OPEN_DRAIN 3

#define GPIO_MODE_INPUT 0
#define GPIO_MODE_OUTPUT_10MHZ 1
#define GPIO_MODE_OUTPUT_2MHZ 2
#define GPIO_MODE_OUTPUT_50MHZ 3

#define PA0 ((pin_t) {.base = GPIOA, .pin = 0})
#define PA1 ((pin_t) {.base = GPIOA, .pin = 1})
#define PA2 ((pin_t) {.base = GPIOA, .pin = 2})
#define PA3 ((pin_t) {.base = GPIOA, .pin = 3})
#define PA4 ((pin_t) {.base = GPIOA, .pin = 4})
#define PA5 ((pin_t) {.base = GPIOA, .pin = 5})
#define PA6 ((pin_t) {.base = GPIOA, .pin = 6})
#define PA7 ((pin_t) {.base = GPIOA, .pin = 7})
#define PA8 ((pin_t) {.base = GPIOA, .pin = 8})
#define PA9 ((pin_t) {.base = GPIOA, .pin = 9})
#define PA10 ((pin_t) {.base = GPIOA, .pin = 10})
#define PA11 ((pin_t) {.base = GPIOA, .pin = 11})
#define PA12 ((pin_t) {.base = GPIOA, .pin = 12})
#define PA13 ((pin_t) {.base = GPIOA, .pin = 13})
#define PA14 ((pin_t) {.base = GPIOA, .pin = 14})
#define PA15 ((pin_t) {.base = GPIOA, .pin = 15})

#define PB0 ((pin_t) {.base = GPIOB, .pin = 0})
#define PB1 ((pin_t) {.base = GPIOB, .pin = 1})
#define PB2 ((pin_t) {.base = GPIOB, .pin = 2})
#define PB3 ((pin_t) {.base = GPIOB, .pin = 3})
#define PB4 ((pin_t) {.base = GPIOB, .pin = 4})
#define PB5 ((pin_t) {.base = GPIOB, .pin = 5})
#define PB6 ((pin_t) {.base = GPIOB, .pin = 6})
#define PB7 ((pin_t) {.base = GPIOB, .pin = 7})
#define PB8 ((pin_t) {.base = GPIOB, .pin = 8})
#define PB9 ((pin_t) {.base = GPIOB, .pin = 9})
#define PB10 ((pin_t) {.base = GPIOB, .pin = 10})
#define PB11 ((pin_t) {.base = GPIOB, .pin = 11})
#define PB12 ((pin_t) {.base = GPIOB, .pin = 12})
#define PB13 ((pin_t) {.base = GPIOB, .pin = 13})
#define PB14 ((pin_t) {.base = GPIOB, .pin = 14})
#define PB15 ((pin_t) {.base = GPIOB, .pin = 15})

#define PC13 ((pin_t) {.base = GPIOC, .pin = 13})
#define PC14 ((pin_t) {.base = GPIOC, .pin = 14})
#define PC15 ((pin_t) {.base = GPIOC, .pin = 15})

void gpio_init(void);
void gpio_mode(pin_t pin, uint8_t mode, uint8_t cnf);
void gpio_write(pin_t pin, uint8_t val);
void gpio_toggle(pin_t pin);
uint8_t gpio_read(pin_t pin);

#endif

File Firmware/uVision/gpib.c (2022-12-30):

#include "gpib.h"
#include "gpio.h"
#include "delay.h"

#define GPIB_ATN PB9
#define GPIB_NDAC PA15
#define GPIB_NRFD PB8
#define GPIB_DAV PB7
#define GPIB_EOI PB5
#define GPIB_REN PB3
#define GPIB_IFC PB4
#define GPIB_SRQ PB6

#define DATA_BUS_WRITE(b) do { GPIOA->CRL = 0x77777777; GPIOA->ODR = (GPIOA->ODR & ~0xFF) | ((uint32_t) b); } while(0) // outputs open-drain
#define DATA_BUS_READ (uint8_t) (GPIOA->IDR & 0xFF)
#define DATA_BUS_RELEASE do { GPIOA->CRL = 0x88888888; GPIOA->ODR |= 0xFF; } while(0) // all as inputs with pull-ups

#define ATN_LOW   do { gpio_mode(GPIB_ATN, GPIO_MODE_OUTPUT_50MHZ, GPIO_CNF_OUTPUT_GENERAL_OPEN_DRAIN); gpio_write(GPIB_ATN, 0); } while(0)
#define ATN_HIGH  do { gpio_mode(GPIB_ATN, GPIO_MODE_INPUT, GPIO_CNF_INPUT_PULL_UP); } while(0)
#define NDAC_LOW  do { gpio_mode(GPIB_NDAC, GPIO_MODE_OUTPUT_50MHZ, GPIO_CNF_OUTPUT_GENERAL_OPEN_DRAIN); gpio_write(GPIB_NDAC, 0); } while(0)
#define NDAC_HIGH do { gpio_mode(GPIB_NDAC, GPIO_MODE_INPUT, GPIO_CNF_INPUT_PULL_UP); } while(0)
#define NRFD_LOW  do { gpio_mode(GPIB_NRFD, GPIO_MODE_OUTPUT_50MHZ, GPIO_CNF_OUTPUT_GENERAL_OPEN_DRAIN); gpio_write(GPIB_NRFD, 0); } while(0)
#define NRFD_HIGH do { gpio_mode(GPIB_NRFD, GPIO_MODE_INPUT, GPIO_CNF_INPUT_PULL_UP); } while(0)
#define DAV_LOW   do { gpio_mode(GPIB_DAV, GPIO_MODE_OUTPUT_50MHZ, GPIO_CNF_OUTPUT_GENERAL_OPEN_DRAIN); gpio_write(GPIB_DAV, 0); } while(0)
#define DAV_HIGH  do { gpio_mode(GPIB_DAV, GPIO_MODE_INPUT, GPIO_CNF_INPUT_PULL_UP); } while(0)
#define EOI_LOW   do { gpio_mode(GPIB_EOI, GPIO_MODE_OUTPUT_50MHZ, GPIO_CNF_OUTPUT_GENERAL_OPEN_DRAIN); gpio_write(GPIB_EOI, 0); } while(0)
#define EOI_HIGH  do { gpio_mode(GPIB_EOI, GPIO_MODE_INPUT, GPIO_CNF_INPUT_PULL_UP); } while(0)
#define REN_LOW   do { gpio_mode(GPIB_REN, GPIO_MODE_OUTPUT_50MHZ, GPIO_CNF_OUTPUT_GENERAL_OPEN_DRAIN); gpio_write(GPIB_REN, 0); } while(0)
#define REN_HIGH  do { gpio_mode(GPIB_REN, GPIO_MODE_INPUT, GPIO_CNF_INPUT_PULL_UP); } while(0)
#define IFC_LOW   do { gpio_mode(GPIB_IFC, GPIO_MODE_OUTPUT_50MHZ, GPIO_CNF_OUTPUT_GENERAL_OPEN_DRAIN); gpio_write(GPIB_IFC, 0); } while(0)
#define IFC_HIGH  do { gpio_mode(GPIB_IFC, GPIO_MODE_INPUT, GPIO_CNF_INPUT_PULL_UP); } while(0)

#define DAV_STATE  gpio_read(GPIB_DAV)
#define NDAC_STATE gpio_read(GPIB_NDAC)
#define NRFD_STATE gpio_read(GPIB_NRFD)
#define ATN_STATE  gpio_read(GPIB_ATN)
#define EOI_STATE  gpio_read(GPIB_EOI)

#define GPIB_DEVICE_CONNECTSTATE_UNKNOWN      (0)
#define GPIB_DEVICE_CONNECTSTATE_DISCONNECTED (1)
#define GPIB_DEVICE_CONNECTSTATE_CONNECTED    (2)


/**********************************************************************************************************
 * STATIC functions
 **********************************************************************************************************/
static uint8_t  volatile timer0_100mscounter;
static uint8_t  timer0_div;
static uint8_t  s_device_state = GPIB_DEVICE_CONNECTSTATE_UNKNOWN;
static uint8_t s_gpib_disconnect_counter;
static volatile bool     s_gpib_transaction_active = false; /* TRUE, if a device is addressed as talker or listener */

static char s_terminator = '\0'; /* \0 = no termination character - EOI only, other options are '\n' or '\r' */
 
static void gpib_recover(void)
{
	gpib_init();
}

static bool gpib_tx(uint8_t dat, bool iscommand, gpibtimeout_t ptimeoutfunc)
{
	bool timedout;
	
	DAV_HIGH;
	NRFD_HIGH;
	NDAC_HIGH;  /* they should be already high, but let's enforce it */
	
	if (iscommand)
		ATN_LOW;
	else
		ATN_HIGH;

	DATA_BUS_WRITE(dat);   /* set Data to data bus */
	delay_us(1); /* wait for data to settle */
		
	/* wait until ready for data acceptance (NRFD=H, NDAC=L)*/
	do
	{
		timedout = ptimeoutfunc();
	}
	while ( (NRFD_STATE == 0) && !timedout); /* wait until ready for data (NRFD to get high) */

	if (!timedout)
	{
		DAV_LOW;
		do
		{
			timedout = ptimeoutfunc();
		}
		while ( (NDAC_STATE == 0) && !timedout ); /* wait until NDAC gets high*/
		DAV_HIGH; 
	}
	
	DATA_BUS_RELEASE; /* release data bus */
	ATN_HIGH;	 
	
	if (timedout)
	{
		gpib_recover();
	}
	return timedout;
}

static bool gpib_dat(uint8_t dat, gpibtimeout_t ptimeoutfunc)
{
	return gpib_tx(dat, false, ptimeoutfunc);
}


static bool gpib_cmd_LAG(uint8_t addr, gpibtimeout_t ptimeoutfunc)
{
	bool result;
	result = gpib_tx((addr & 0x1f) | 0x20, true, ptimeoutfunc);
	if (addr & 0xe0)
	{ /* send a secondary address? */
		result = gpib_tx(0x60, true, ptimeoutfunc);        // SAG (SA0)
	}
	return result;
}

static bool gpib_cmd_SECADDR(uint8_t addr, gpibtimeout_t ptimeoutfunc)
{
	return gpib_tx(addr | 0x60, true, ptimeoutfunc);
}


static bool gpib_cmd_TAG(uint8_t addr, gpibtimeout_t ptimeoutfunc)
{
	bool result;
	result = gpib_tx((addr & 0x1f) | 0x40, true, ptimeoutfunc);
	if (addr & 0xe0)
	{ /* send a secondary address? */
		result = gpib_tx(0x60, true, ptimeoutfunc);        // SAG (SA0)	
	}
	return result;
}

static bool gpib_cmd_UNL(gpibtimeout_t ptimeoutfunc)
{
	return gpib_tx(0x3F, true, ptimeoutfunc);
}

static bool gpib_cmd_UNT(gpibtimeout_t ptimeoutfunc)
{
	return gpib_tx(0x5F, true, ptimeoutfunc);
}

static bool gpib_cmd_LLO(gpibtimeout_t ptimeoutfunc) // local lockout
{
	return gpib_tx(0x11, true, ptimeoutfunc);
}

static bool gpib_cmd_GTL(gpibtimeout_t ptimeoutfunc) // goto local
{
	return gpib_tx(0x01, true, ptimeoutfunc);
}


static bool gpib_cmd_SPE(gpibtimeout_t ptimeoutfunc) // serial poll enable
{
	return gpib_tx(0x18, true, ptimeoutfunc);
}

static bool gpib_cmd_SPD(gpibtimeout_t ptimeoutfunc) // serial poll disable
{
	return gpib_tx(0x19, true, ptimeoutfunc);
}

static bool gpib_cmd_GET(gpibtimeout_t ptimeoutfunc) // group execute trigger (addressed command)
{
	return gpib_tx(0x08, true, ptimeoutfunc);
}



uint8_t gpib_readStatusByte(uint8_t addr, gpibtimeout_t ptimeoutfunc)
{
	bool timedout, eoi;
	uint8_t status;
	
	timedout = false;
	status = 0;
	
	if (!timedout)
		timedout = gpib_cmd_SPE(ptimeoutfunc);
	if (!timedout)
		timedout = gpib_cmd_TAG(addr, ptimeoutfunc); 
	ATN_HIGH; /* make ATN H */	
	NDAC_LOW;   /* make NDAC L */

	if (!timedout)
		status = gpib_readdat(&eoi, &timedout, ptimeoutfunc);
	
	if (!timedout)
		timedout = gpib_cmd_UNT(ptimeoutfunc); 
	if (!timedout)
		timedout = gpib_cmd_SPD(ptimeoutfunc);
	if (timedout)
		gpib_recover();	
	return status;
}

bool gpib_localLockout(gpibtimeout_t ptimeoutfunc)
{
	bool timedout;

	timedout = gpib_cmd_LLO(ptimeoutfunc);
	if (timedout)
		gpib_recover();
	return timedout;
}

bool gpib_gotoLocal(uint8_t addr, gpibtimeout_t ptimeoutfunc)
{
	bool timedout;
	
	timedout = gpib_cmd_LAG(addr, ptimeoutfunc); 
	if (!timedout)
		timedout = gpib_cmd_GTL(ptimeoutfunc);
		
	if (!timedout)
		timedout = gpib_cmd_UNL(ptimeoutfunc);
		
	if (timedout)
		gpib_recover();

	return timedout;
}


bool gpib_trigger(uint8_t addr, gpibtimeout_t ptimeoutfunc)
{
	bool timedout;
	
	timedout = gpib_cmd_LAG(addr, ptimeoutfunc); 
	if (!timedout)
		timedout = gpib_cmd_GET(ptimeoutfunc);
	if (!timedout)
		timedout = gpib_cmd_UNL(ptimeoutfunc);
		
	if (timedout)
		gpib_recover();
	return timedout;
}


/*
static bool gpib_cmd_DCL(gpibtimeout_t ptimeoutfunc) // device clear
{
	return gpib_tx(0x14, true, ptimeoutfunc);
}

static bool gpib_cmd_SDC(gpibtimeout_t ptimeoutfunc) // selective device clear
{
	return gpib_tx(0x04, true, ptimeoutfunc);
}
*/

static void timer_init(void)
{
	//TCCR0B = 5; // Prescaler 1024 = 15625 Hz
	// Overflow Interrupt erlauben
	//TIMSK0 |= (1<<TOIE0);
	timer0_div = 0;
	timer0_100mscounter = 0;
}


void TIM2_IRQHandler(void)
{
	timer0_div++;
	if (timer0_div >= 6) /* are 100ms passed? */
	{
		timer0_100mscounter++;
		timer0_div = 0;
		
		if (!s_gpib_transaction_active) /* only check, if no GPIB transaction is active */
		{
			if (!ATN_STATE) /* is ATN LOW? This can only happen if no GPIB device is connected/powered */
			{
				if (s_gpib_disconnect_counter == 2)
				{ /* after 100-200ms with ATN low, assume, that there is no GPIB device connected */
					s_device_state = GPIB_DEVICE_CONNECTSTATE_DISCONNECTED;
				}
				else
				{
					s_gpib_disconnect_counter++;
				}
			}
			else
			{ /* device is connected */
				s_gpib_disconnect_counter = 0;
				s_device_state = GPIB_DEVICE_CONNECTSTATE_CONNECTED;
			}
		}
	}
}



/**********************************************************************************************************
 * global API functions
 **********************************************************************************************************/

void gpib_init(void)
{
// PB5 = REN
	DATA_BUS_RELEASE;
	ATN_HIGH;
	NDAC_HIGH;
	DAV_HIGH;
	EOI_HIGH;
	IFC_HIGH;
	gpio_mode(GPIB_SRQ, GPIO_MODE_INPUT, GPIO_CNF_INPUT_PULL_UP);
	
  REN_LOW;	/* remote enable */

	s_gpib_transaction_active = false;
	s_gpib_disconnect_counter = 0;
	
	gpib_interface_clear();
	timer_init(); /* init timeout timer */
}

bool gpib_is_connected(void)
{
	return s_device_state == GPIB_DEVICE_CONNECTSTATE_CONNECTED;
}

void gpib_ren(bool enable)
{
	if (enable)
	{
		REN_LOW; /* remote enable */
	}
	else
	{
		REN_HIGH; /* remote disable */
	}
}




void gpib_interface_clear(void)
{
	IFC_LOW; /* interface clear */
	delay_ms(100);
	IFC_HIGH; /* interface clear */
	delay_ms(10);
	s_gpib_transaction_active = false;
}
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
